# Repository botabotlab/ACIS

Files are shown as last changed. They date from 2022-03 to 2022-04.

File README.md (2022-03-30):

# AMIS
AMIS : an open-source Autonomous MultiWell Imaging Station



# Build instructions

## Server

The following software must be installed for the server to work properly. The installation has been tested on different machines with ARM or X86 architecture based on Ubuntu or Debian distributions:

-   **[Mosquitto](https://github.com/eclipse/mosquitto)** : allows devices to communicate with each other using the MQTT protocol)
-   **[NodeJS 16](https://github.com/nodejs/Release)** (recommended version) : required runtime for the automation software
-   **[Node-RED](https://github.com/node-red/node-red)** : (automation server and graphical interface
-   **[Motion](https://github.com/Motion-Project/motion)** (not mandatory) : allows the creation of an IP camera to remotely retrieve the video stream from the microscope.
-   **[v4l2loopback](https://github.com/umlaeute/v4l2loopback)** : creation of virtual cameras that can be used for autofocus, image analysis, image display on screen or as an IP camera.
-   **[ffmpeg](https://github.com/FFmpeg/FFmpeg)** : duplicate the video stream of the USB camera in the virtual cameras
-   **[OpenCV-python](https://github.com/opencv/opencv-python)** : Image analysis library (python3 required)
    
Once Node-RED is installed and started, the user can access its graphical interface directly from the single board computer by entering http://127.0.0.1:1880 in the web browser or http://local.ip.of.the.SBC:1880 (if the interface is accessed from another computer). The "**[node-red-dashboard](https://github.com/node-red/node-red-dashboard)**" palette must be installed and the flow can be imported.

## Microcontroller

### Dependencies 

The microcontrollers code compilation and uploading can be done using the Arduino IDE. However, the Arduino IDE does not natively work with the ESP8266. The support for these boards must therefore be manually added by going to **File > Preference > Additional Boards Manager URLs** and pasting the following URL: "http://arduino.esp8266.com/stable/package_esp8266com_index.json" and installed by selecting ESP8266 in **Tools > Board > Boards Manager.**

3 libraries are required to run the code and can be found in the Arduino IDE library manager:

-   [PubSubClient](https://github.com/knolleary/pubsubclient)
-   [ArduinoJson](https://github.com/bblanchon/ArduinoJson)
-   [Adafruit_NeoPixel](https://github.com/adafruit/Adafruit_NeoPixel)
    
### SPIFFS 

To facilitate the setting of WiFi and restore the previous state of the LEDs even in case of the microcontroller restart, JSON files (wifi.json and state.json) are stored in the SPIFFS memory. The use of SPIFFS memory allows to modify these parameters without having to recompile and upload the code and the use of JSON files makes the editing of these files faster and more intuitive than modifying the source code. Access to SPIFF memory is also not integrated by default in the IDE. The ESP8266 file uploader plugin can be downloaded at the following address:

https://github.com/esp8266/arduino-esp8266fs-plugin and unzipped in a **"tools"** folder created in the working directory of the arduino IDE.

The folder structure should look like this : **< home_dir>/Arduino-<version> /tools/ESP8266FS/tool/esp8266fs.jar)**. The arduino IDE can then be restarted and the tool should appear in **Tool > ESP8266 Sketch Data Upload.**

## Microscope

### Camera support

The camera support has been 3D printed in translucent ABS using a Prusa I3 MK3 (nozzle : 250°C, Bed : 100°C, nozzle 0.4mm, layer height : 0.2mm, filling 100%), however the parts can be printed in any type of plastic (PLA, PETG,...) using printers with lower tolerances and precision. The distance between the lens and the sensor is not critical, but the lens must be perpendicular to the sensor as well as the camera which must be perpendicular to the sample to avoid optical aberrations on the edge of the images. A manual adjustment of the parts using sandpaper may be necessary to compensate for small printing imperfections. The camera is held on the X axis of the printer with 3 neodymium magnets of 10x3mm.

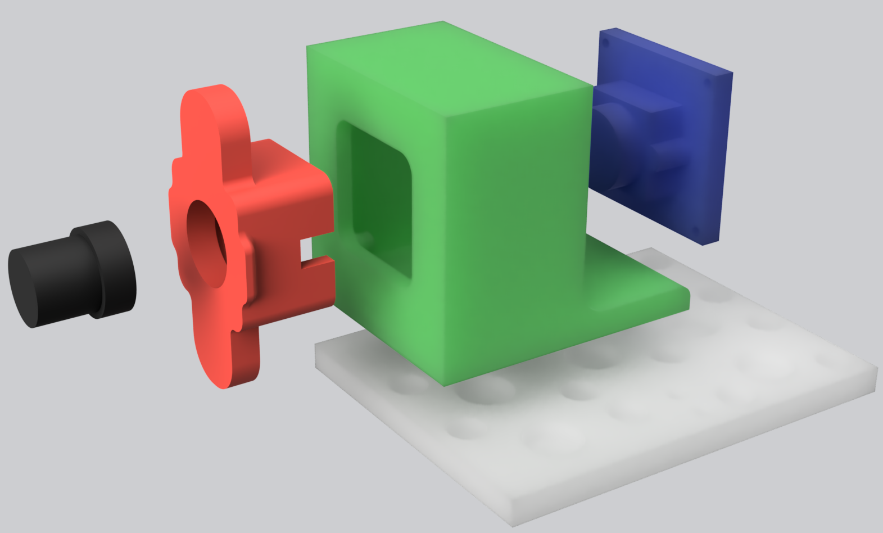
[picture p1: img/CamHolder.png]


Several digital camera models with different prices, sizes and resolutions were tested to realize the microscope. The following sensors (with prices ranging from 10€ to 50€) were tested : Omnivision OV2640, OV3660, OV4689 and OV5647 or Sony IMX179 and all gave similar results. We have also modified webcams that are easily found on the market such as Logitech c270 or c920 which work perfectly. However, we recommend the use of camera modules with an M12 mount compared to webcams ; the lens placement is easier and the generally square PCB (versus rectangular/oval for webcams) makes it easier to install the camera on the magnetic mount. The resolution has little importance on the captured image quality, although a higher resolution allows a greater digital zoom. The limiting system factor is not the sensor, but the optics. A resolution of 720p is thus largely sufficient and allows simplifying the image analysis, but a 1080p or 4k resolution can be used in case the user would like to perform a digital zoom in addition to the optical zoom. 

### Light

The lighting system is built by soldering 24 addressable LED SK6812 (Data OUT of one LED should be soldered on the Data In of the next one) the LED matrix thus created will be driven by an ESP8266 by soldering the VCC and GND of the LEDs on pin 5V and GND of the microcontroller and by connecting the Din of the first led on pin D5 (GPIO 14) of the ESP. The system will then be controllable in MQTT by the Node-RED server. 

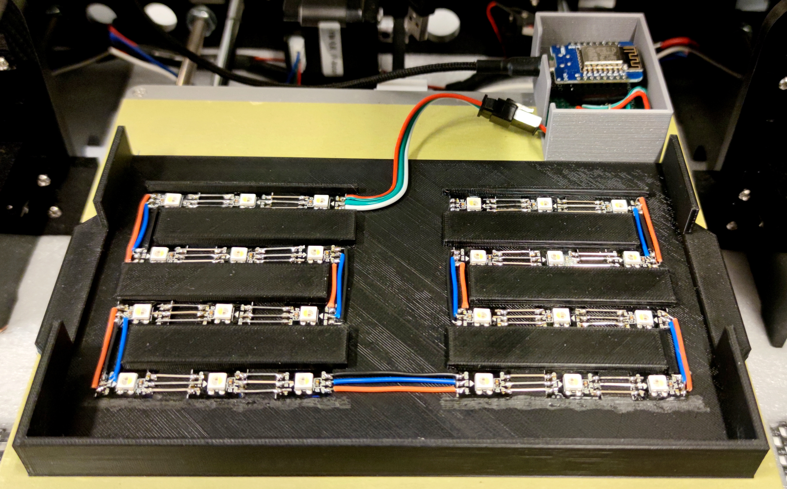
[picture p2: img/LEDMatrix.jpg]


The LED employed offer 4 light channels ; red, green, blue and cold white. We recommend using RGBW LED rather than RGB LED such as WS2812B. Although it is possible to obtain a relatively white light by combining the 3 RGB channels the positioning in 3 diodes makes that the light of each channel does not enter the medium with exactly the same angle of incidence and thus does form chromatic aberrations  These aberrations are not critical as the colored background will be removed by the thresholding adaptation step of the image analysis algorithm but it may affect the measurements if a quantification of the color of the algae is desired. The presence of a white channel mitigates this problem while offering a higher light intensity and preserving the accuracy of the colors (we recommend choosing SK6812 Neutral white and locking the white balance of the camera) . The color channels can be used to expose the sample to monochromatic or polychromatic light in order to improve the image contrast or to induce certain biological processes.

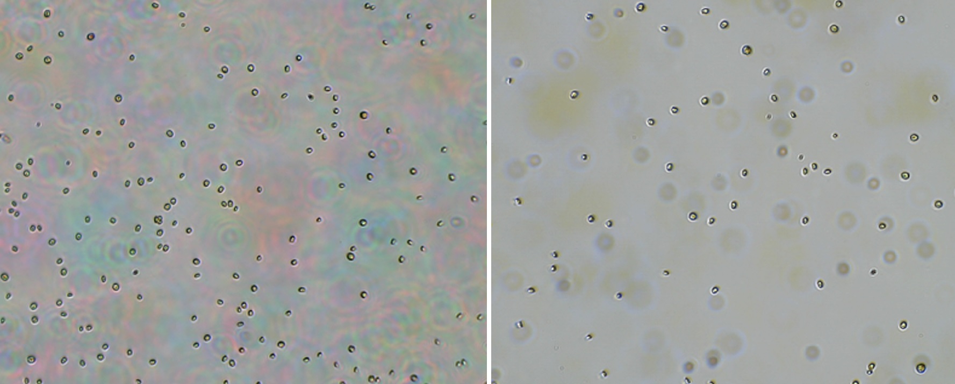
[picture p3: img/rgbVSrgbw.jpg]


*Chromatic aberration caused by the RGB light compared to a sample illuminated by a white light.*

## Pump

The system use a pump system described in a  [previous publication](https://www.sciencedirect.com/science/article/pii/S2468067221000286) . For the microscope, only one pump is needed and can be connected to a culture vessel (Erlenmeyer flask, photobioreactor) using a 7mm diameter autoclavable silicone tube. The tubing can be inserted into a micropipette tip for P1000 (blue tip). The pump can be primed until the liquid reaches the tip. The tip can then be placed on the magnetic tool holder and held in place with a 3D printed holder.

[Repository of the pump system](https://doi.org/10.17605/OSF.IO/ZP2S6) 

## 3D printer 

Our goal is to make a simple and universal system that can work with virtually any 3D printer model. A custom PCB would be complex, expensive and not very scalable. We therefore decided to exploit a common feature shared by many 3D printers. Indeed, these printers are generally controllable with standardized commands called GCODE. This set of instructions allows to control the machine movements on its 3 axes and to activate tools (plastic extruder, heating plate, fan, etc.).

Examples of GCode commands :
-   G91 : to set the machine in relative displacement
-   G0 X50 (move 50 mm along the x axis)

 [More info about GCode](https://reprap.org/wiki/G-code)

The commands can be sent via USB or placed in a text file on an SD card (or USB key) that will be read by the machine. 

A 3D printer only applies a simple sequence of commands and has no preconceived notions about their functions. It is therefore totally possible to remove the plastic extruder and replace it with a microscope and still be able to drive the machine using exactly the same commands. This is very interesting as it means that it is possible to transform a printer into a microscope, regardless of its brand, with almost no software or hardware modifications and to restore the original function of the machine if necessary.

### 3D printer hack

We chose an Anet A8 printer because its design is very simple, this model is easy to find on the internet and there are a lot of replacement parts and upgrades available. We kept most of the original parts (chassis, motors, print bed, motherboard). Instead of installing the extruder on the X axis we placed a 3D printed part with magnets to make a quick attachment for the camera or the sampling system. This part has been custom made for the Anet A8 and can not be used for another brand. However this modification is trivial and can be done on any 3D printer of the Cartesian or delta type. The only requirement is to have the camera perpendicular to the print bed (usually the Y axis).

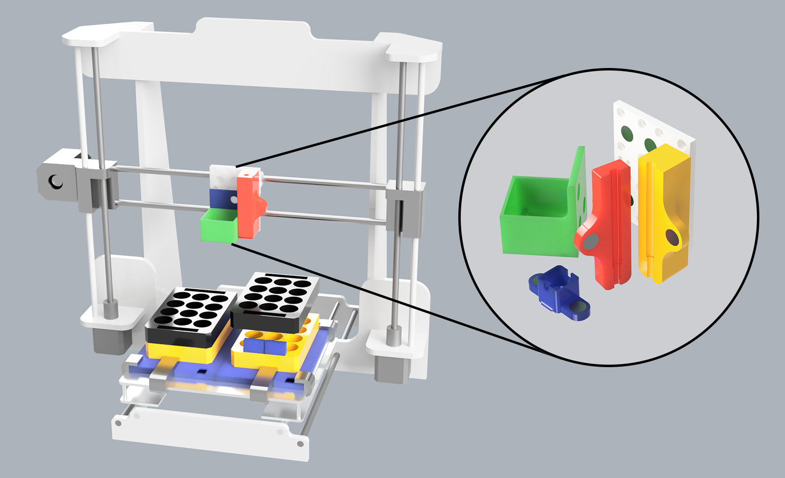
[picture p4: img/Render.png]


To automate and control the device remotely, we connected an ESP8266 on the serial port of the motherboard. This WiFI microcontroller, allows to send Gcode commands using the MQTT communication protocol. The communication is bidirectional, and it is therefore possible to control the machine but also to obtain information on its status such as the current position of the camera (an interesting feature to control the machine remotely). The microcontroller is removable connected to the motherboard using an FC10P  connector and can easily be removed to restore the printer original functions.



*Modification of the Anet A8 motherboard to be able to drive it in MQTT via its serial port. The motherboard has been set in "Serial" mode by bridging two pads (A) and then an ESP8266 (C ) has been connected to the VCC, GND, TX, RX of the motherboard (B). The serial connection between the microcontroller must be "crossed", meaning the TX of the ESP8266 connects to the RX of the motherboard and the RX connects to the TX.*

### Remote control using MQTT

MQTT (Message Queuing Telemetry Transport) is a publish/subscribe machine to machine communication protocol invented by IBM. Initially designed to retrieve information from remote locations from resource constrained devices (like as microcontroller) over an unreliable, high latency and low bandwidth connection (satellite connection for instance) (REF 29) this protocol is nowadays mainly used for IOT (Internet Of Things) applications. This widely used protocol offers numerous advantages for our application. It its simple to use, secure (message can be encrypted using TLS) , reliable, lightweight (in term of computing resources and bandwidth usage), compatible with virtually any programming languages (python, C, C#, C++, java, javascript, lua, ruby, rust, …) and highly scalable.

A typical MQTT communication requires at least 4 components:
-   **Publisher** :  the device that will send information or commands (a computer, a smartphone, a microcontroller)
-   **Subscriber** : the device that will receive the command (in our case a microcontroller connected to the robot)
-   **Broker** : the server that links the different devices
-   **Internet router**
    
*A publisher can also subscribe to one or more topics and that a bidirectional communication between the devices is possible*.

In most universities and corporate networks, some ports may be blocked (even locally) which will prevent MQTT (running on port 1883) from working. We recommend using a router over which the user has full control to create a local subnet to which devices can connect without restriction. The use of an ESP32/8266, a smartphone or a computer in access point mode can also be a solution to create a local network. An internet connection is not necessary as long as all devices are on the same network and port 1883 is not blocked. Our system is able to work locally without depending on a cloud, but an internet connection can be useful for remote control using a VPN (Virtual Private Network) or to host the broker in a VPS (Virtual Private Server).

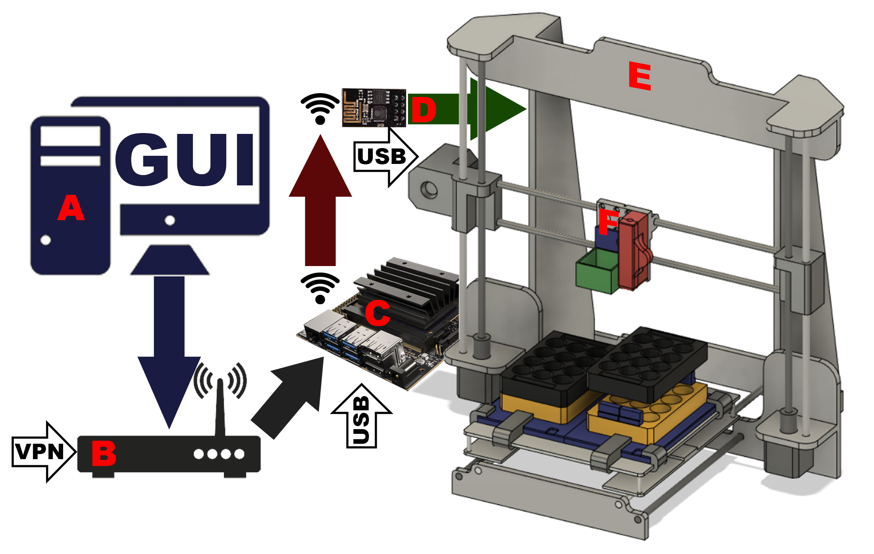
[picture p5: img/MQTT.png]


*Representation of the MQTT communication, allowing to control the microscope remotely. The graphical control interface accessible from a computer or a smartphone (A) connected to the laboratory router (B) allows formatting and send GCODE commands in WiFi to the MQTT broker installed on the Jeston Nano (C ) . The message is then connected to the ESP8266 (D) subscribed to the right topic and which will finally transmit the GCODE command in serial to the printer motherboard (E) allowing to move the camera (F).*

To send a command to the microscope, the user must publish the payload containing the command (e.g. G0 X50) with the topic corresponding to the microscope (microscope/room01/cmd/01) while being subscribed to the debug topic (microscope/room01/debug/01) to receive confirmation that the command is correct and has been applied. For our device, the microscope, the LED lighting system and the manipulation system are all 3 controllable by MQTT.

If the user does not want to use a MQTT connection, our microscope can be completely controlled using a serial communication. Simply connect the signle board computer to the 3D printer using an usb cable and replace the MQTT node with a Serial out node (by installing the "node-red-node-serialport" node) and select the com port (e.g. /dev/ttyUSB0) and baud rate (115200). Since the commands sent have the same structure as GCODE commands, no software modification is necessary. The same applies to the LED array, which can be connected to the Jetson nano via USB and driven via serial.

# Control

The control of the machine can be done in three different ways:

-   Manual remote control by sending messages in MQTT using the software/programming language chosen by the user
-   Manual control from the Node-RED graphical interface
-   Automatic control using a JSON config file

## MQTT Custom control

The two following examples of topics "**microscope/01/move**" and "**microscope/01/light**" manage respectively the microscope and the lighting system thanks to the MQTT Custom control.

The commands sent to the topic "microscope/01/move" must have exactly the same structure as GCODE commands. 

|CMD|Description  |
|--|--|
| M17 | Enable stepper motors |
|M18 | Disable stepper motors|
|M112 | Emergency stop|
|M114 | Get current position|
|G28 | Home|
|G90 | Absolute positioning|
|G91 | Relative positioning|
|G1Axis[X/Y/Z] Position(mm) Feed(optional) | Movement (Ex : G1 X10 Y20 Z30)|
    
*Frequently used GCODE commands*

## Graphical user interface

Once the Node-RED server is launched and the provided flow is deployed, the user can go to the address **http://server.ip:1880/ui** using a smartphone or computer and to access the Node-RED GUI.

*Graphical control interface via Node-RED composed of 5 panels (debug cam, light, control, plate and cam). The first panel (A) allows access to the security camera (Cam) to remotely view the machine to ensure it is working properly or to access the microscope image (Microscope) to observe the samples. The second panel allows to control the light either by choosing a color with the color picker (B) or by manually entering the RGB values (C). The control panel (D) allows you to manually move the camera on its 3 axes and returns the current position of the camera. The flat menu (E) allows you to move the camera to pre-programmed positions or to choose which well to light. The "SP" (safe position) button sends the camera to the upper right corner of the robot and advances the plate towards the user, thus facilitating the installation of multi-well plates, while the "LP" (last position) button returns the camera to its previous position (in case the user accidentally moves the camera). The panel (F) allows you to name the images. If several images are captured, the name will automatically be changed by adding the number of the photo (Iter). Finally, panel (G) allows you to perform autofocus and also to program the taking of multiple images separated by a defined delay.*

The camera can be started on the "**Developper camera**" menu. 

*The "Create virtual Cam" button allows to use “v4l2loopback” to create virtual cameras that will be used by different capture, image analysis, autofocus or debugging programs in HDMI or via IP stream. The use of virtual cameras is necessary because several programs cannot access the same camera at the same time. The second button allows to launch motion which will create an IP stream allowing to access the images remotely in the graphical interface. The button "copy usb webcam" will launch “ffmpeg” which will clone the physical camera in the different virtual cameras. The buttons CAM LCD ON and OFF allow the microscope image display or hiding through HDMI. Analyze ON and OFF display the image analysis (counting and size measurement) in real time on the HDMI output . Finally, the WB lock button and the WB slider allow to lock the white balance to a fixed value defined by the user. When the system is functional the 3 menus should be green.*

This graphical interface allows a quick and manual observation, capture and analysis of one or more samples. A typical use would be to place different samples in multi-well plates, turn on the microscope, initialize the cameras, send the camera to "**Safepos**", place the plates on the bed, choose the illumination color and observe the desired samples. This system is faster than a regular microscope using a slide/coverslip system. 

## Automation

Many situations may require the capture of a large number of images (capture of several plates in a row) or need to be done over a long period of time (real time monitoring of a culture). As manually preparing and analyzing the samples is not feasible in this case, we have developed an automation system. This system allows to automate all the actions available on the graphical interface based on a JSON structure that is both intuitive and flexible. The user can thus define the sequence name, the wells to fill (if filling is desired) and the need to purge the circuit or not (to avoid contamination if the time between two samples is high), the wells to capture (if capturing is desired) and the light (color and intensity) corresponding to each well and the time between two samplings or captures.

JSON structure :

	{  
	"name" : "Name of the experiment",  
	"pos" : [ [X1 (0-5) ,Y1(0-3)] ],  
	"light": [ [R(0-255) , G(0-255) , B(0-255), W(0-255)] ],  
	"delay":[(s)],  
	"capture":true-false,  
	"sampling":true-false,  
	"volume":[(ml)]  
	"trash":true-false  
	}

The order of the wells can be defined by the user and not all wells have to be used ; it is possible to fill a complete plate or just a column. The light can be different between each well. To do this it is imperative that the "light" array has exactly the same length as the "pos" array. If the same color intensity should be used for all wells it is possible to enter only one light value in "light" and the system will automatically apply the light to all wells.

It is not mandatory to capture images ; the machine can for example be used to fill multi-well plates with samples. To do so, you just have to set the "capture" key to false. The following JSON allows to fill 1 multiwell plate with a volume of 2ml (this procedure takes about 2 minutes for 12 wells). Capturing images alone without taking a sample is also possible ; the "capture" property must be set to true.

Demo script to fill the plate 1 with samples of 1ml : 

	{
	"name" : "Fill plate 1",
	"pos":[
	[0,0],[1,0],[2,0],
	[0,1],[1,1],[2,1],
	[0,2],[1,2],[2,2],
	[0,3],[1,3],[2,3]
	],
	"sampling":true,
	"volume" : [1]
	} 

Demo script to capture the plate 1 with a white light of 100% :

	{
	"name" : "Capture plate 1",
	"pos":[
	[0,0],[1,0],[2,0],
	[0,1],[1,1],[2,1],
	[0,2],[1,2],[2,2],
	[0,3],[1,3],[2,3]
	],
	"capture":true,
	"light":[[0,0,0,255]]
	}

### Example

The following example describes the most complex measurement sequence currently achievable with the machine consisting in reading three samples with different parameters. The robot will automatically fill the wells with three different volumes (1ml 2ml and 3ml) while purging the silicone tube between two samples. Each sample will be observed with a different color (red, green and blue) and intensity (100%, 50% and 25%) and the time between two measurements is set to 30 seconds for the first sample sample and 1 minute for the second one : 

	{
	"name" : "DemoSeq", 
	"pos" : [[0,0],[2,3],[3,0]], 
	"light" : [[255,0,0,0],[0,255,0,0],[0,0,255,0]], 
	"delay" : [30,60,0] , 
	"sampling" : true, 
	"volume" : [1,2,3], 
	"trash" : true, 
	"capture" : true
	}

## Safety

- The system uses a 220V power supply so the connections must be properly isolated. 
- The motherboard as well as the single board computer and the lighting system must be kept away from humidity or any conductive elements that could cause a short circuit. 
- The 3 axes of movement must not be obstructed as most 3D printers do not have built-in stall detection (meaning that the motors can be forced even if they are blocked) and the limit switches must be accessible during calibration. 
- The user must always check that the magnets are well aligned when a tool is placed on the machine, taking care not to get his fingers caught when installing the tools as the magnets are relatively powerful.

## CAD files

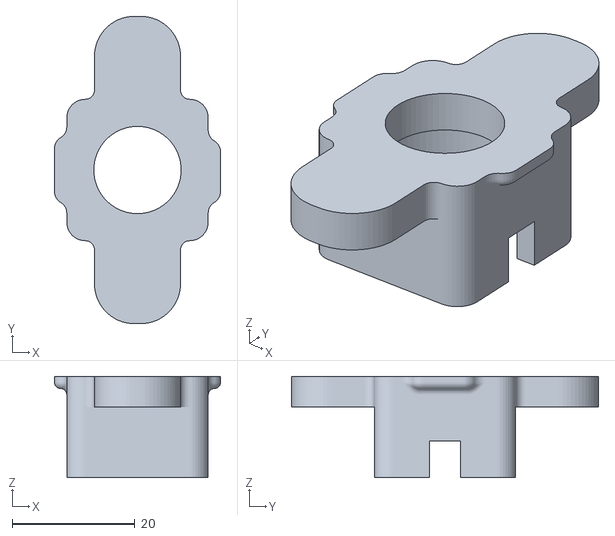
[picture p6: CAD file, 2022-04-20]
3Dfiles/Lens_holder_V2.stl
27.0 x 50.0 x 16.5

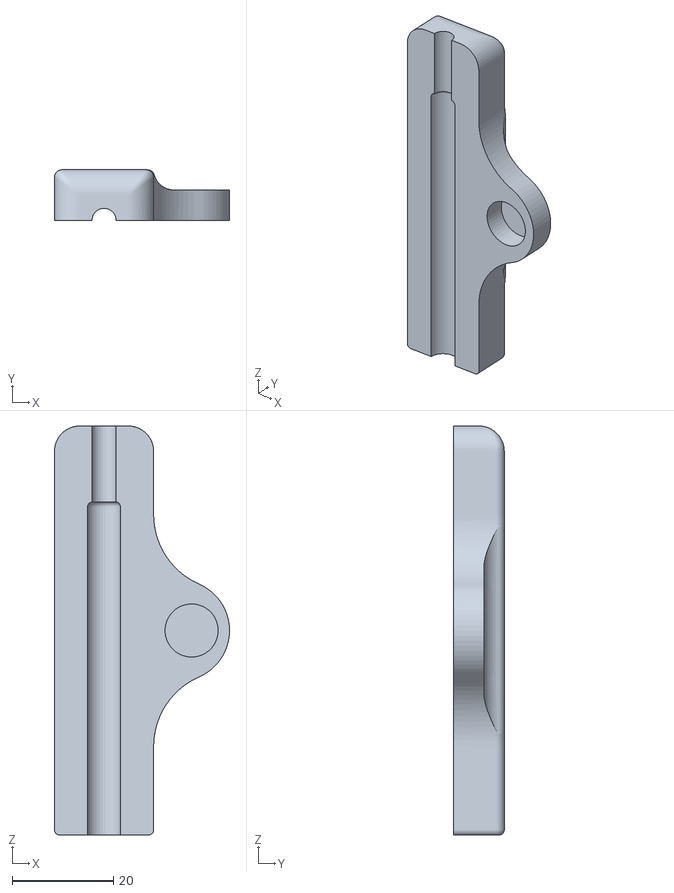
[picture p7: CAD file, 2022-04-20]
3Dfiles/Pipette_V1B.stl
34.6 x 10.0 x 80.8

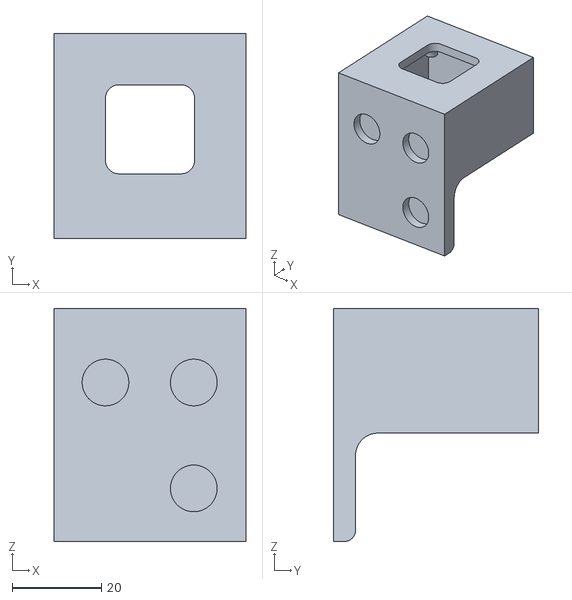
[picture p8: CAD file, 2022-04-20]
3Dfiles/Cam_body_V1.stl
43.0 x 46.2 x 52.4

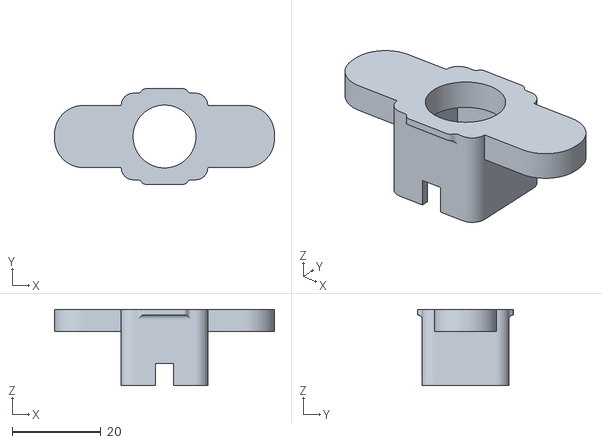
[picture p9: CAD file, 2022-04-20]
3Dfiles/Lens_holder_V1.stl
49.5 x 21.5 x 17.2

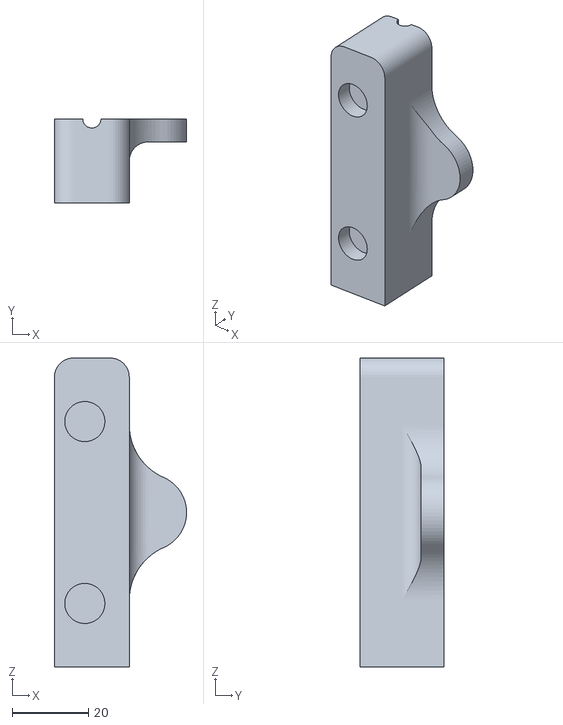
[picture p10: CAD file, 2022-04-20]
3Dfiles/Pipette_V1A.stl
34.6 x 22.0 x 80.8

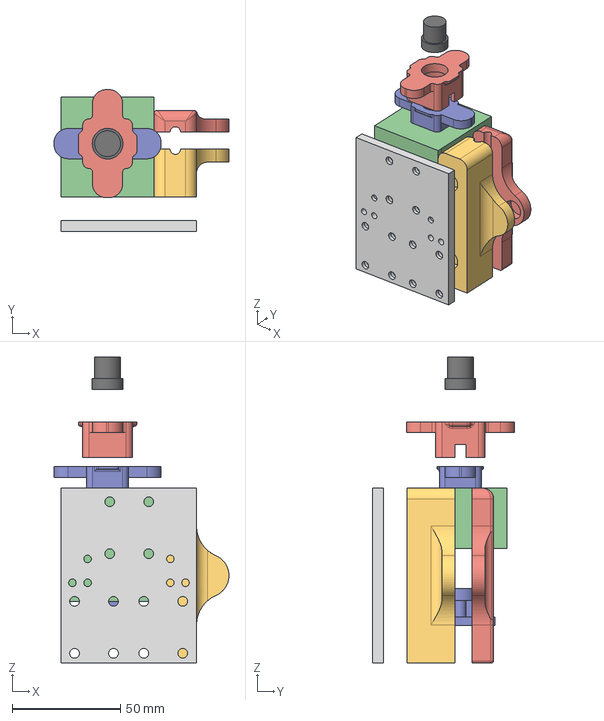
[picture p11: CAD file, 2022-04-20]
3Dfiles/Camera_Pipette_magnetic-holder.step
80.9 x 65.6 x 141.4 mm

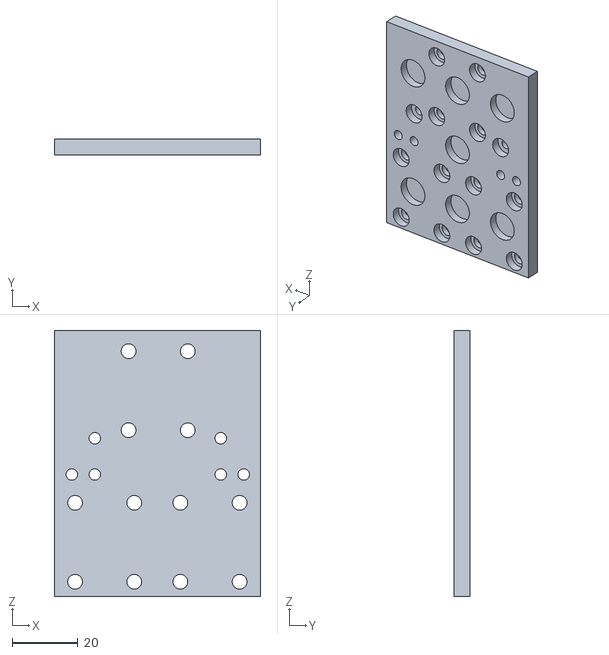
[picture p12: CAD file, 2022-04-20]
3Dfiles/AnetA8_magnetic_holder.stl
62.7 x 5.00 x 80.8

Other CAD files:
3Dfiles/Cam_body_V2.stl

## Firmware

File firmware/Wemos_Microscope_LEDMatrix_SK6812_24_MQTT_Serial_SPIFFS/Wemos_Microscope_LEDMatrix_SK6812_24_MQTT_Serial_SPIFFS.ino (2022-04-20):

//Dependencies
//--------------------------------------
#include <Arduino.h>
#include <ESP8266WiFi.h>
#include <WiFiClient.h>
#include <ESP8266WebServer.h>
#include <PubSubClient.h>
#include <DNSServer.h>
#include "FS.h"
#include <ArduinoJson.h> //ArduinoJSON6
#include <Adafruit_NeoPixel.h>
//--------------------------------------

//WiFi Settings
//----------------------------------------------------------------------------------------
const IPAddress apIP(192, 168, 1, 1);
const char* apSSID = "Microscope_SK6812";
boolean SettingMode = false;
String ssidList;
int maxtry = 30;
DNSServer dnsServer;
ESP8266WebServer webServer(80);
const char *ssid, *password, *mqtt_server, *mqtt_user, *mqtt_pass, *topic_led, *topic_all, *HostName;
DynamicJsonDocument WIFI(2048);

WiFiClient espClient;
PubSubClient client(espClient);
bool WiFiConnected = false;
//----------------------------------------------------------------------------------------

//#define FASTLED_INTERNAL

#define NUM_LEDS 24
#define LED_PIN 14
Adafruit_NeoPixel LED(NUM_LEDS, LED_PIN, NEO_GRBW + NEO_KHZ800);
//CRGB LED[NUM_LEDS];

DynamicJsonDocument CMD(2048);
DynamicJsonDocument STATE(2048);

int MatrixPos[][6] = {
  {2,1,0,23,22,21},
  {3,4,5,18,19,20},
  {8,7,6,17,16,15},
  {9,10,11,12,13,14},
};

//MQTT
//-------------------------------------------------------------------
void MQTT_loop() {
  if (WiFiConnected == true) {
    if (!client.connected()) {
      reconnect();
    }
    client.loop();
  }
}

void callback(String topic, byte* message, unsigned int length) {
  String messageTemp;
  for (int i = 0; i < length; i++) {
    messageTemp += (char)message[i];
  }
  Serial.print("Topic : ");
  Serial.println(topic);
  Serial.print("Payload : ");
  Serial.println(messageTemp);
  Settings(topic, messageTemp);
}
//-------------------------------------------------------------------

//LED Settings
//-------------------------------------------------
void Settings(String topic, String messageTemp) {
  deserializeJson(CMD, messageTemp);
  int X = 0, Y = 0, R = 0, G = 0, B = 0, W = 0;
  if (CMD.containsKey("R")) {
    R = CMD["R"];
  }
  if (CMD.containsKey("G")) {
    G = CMD["G"];
  }
  if (CMD.containsKey("B")) {
    B = CMD["B"];
  }
  if (CMD.containsKey("W")) {
    W = CMD["W"];
  }
  if (CMD.containsKey("X")) {
    X = CMD["X"];
  }
  if (CMD.containsKey("Y")) {
    Y = CMD["Y"];
  }
  if (topic == topic_led) {
    //LED[MatrixPos[Y][X]] = CRGB( R, G, B);
    LED.setPixelColor(MatrixPos[Y][X], LED.Color(R, G, B , W));
    STATE[MatrixPos[Y][X]]["R"] = R;
    STATE[MatrixPos[Y][X]]["G"] = G;
    STATE[MatrixPos[Y][X]]["B"] = B;
    STATE[MatrixPos[Y][X]]["W"] = W;
    save_state();
  }
  if (topic == topic_all) {
    //fill_solid(LED, NUM_LEDS, CRGB( R, G, B));
    LED.fill(LED.Color(R, G, B , W), 0, NUM_LEDS);
    for (int i = 0; i < 25; i++) {
      STATE[i]["R"] = R;
      STATE[i]["G"] = G;
      STATE[i]["B"] = B;
      STATE[i]["W"] = W;
    }
    save_state();
  }
  //FastLED.show();
  LED.show();
}

//-------------------------------------------------
void setup() {
  //FastLED.addLeds<WS2811, DATA_PIN, GRB>(LED, NUM_LEDS);
  LED.begin();
  Serial.begin(115200);
  Serial.println();
  Serial.setTimeout(500);

  if (!SPIFFS.begin()) {
    Serial.println("An Error has occurred while mounting SPIFFS");
    return;
  }

  load_wifi();
  WiFiConnected = setup_wifi();
  client.setServer(mqtt_server, 1883);
  client.setCallback(callback);
  load_state();
  restore_state();
}

void loop() {
  MQTT_loop();
  if (Serial.available()) {
    String input = Serial.readString();
    String Select = input.substring(0, 1);
    String Command = input.substring(1);

    //HELP
    //....................................
    if (Select == "H" || Select == "h") {
      Serial.println("-------------------------------------------------------------");
      Serial.println("Available commands :");
      Serial.println("H or h : Help");
      Serial.println();
      Serial.println("R or r : Start a Web UI to edit de WiFi/MQTT settings");
      Serial.println();
      Serial.println("W or w + JSON: Edit the WiFi/MQTT With the provided JSON");
      Serial.println("Example : W {\"SSID\": \"WiFi SSID\", \"Pass\":\"WiFi Pass\", \"MQTT_Server\":\"Broker.IP\", \"MQTT_Pass\":\"Broker.Pass\", \"Topic_LED1\":\"topic/led/01\", \"Topic_LED2\":\"topic/led/02\", \"HostName\":\"HostName\"}");
      Serial.println();
      Serial.println("A or a + JSON : Control the whole box");
      Serial.println("A {\"R\":0-255, \"G\":0-255, \"B\":0-255, \"W\":0-255 }");
      Serial.println("Example : A {\"R\":255, \"G\":0, \"B\":0, \"W\":0 }");
      Serial.println();
      Serial.println("XYRGB JSON : Control one LED");
      Serial.println("{\"X\": 0-4, \"Y\": 0-4, \"R\":0-255, \"G\":0-255, \"B\":0-255, \"W\":0-255 }");
      Serial.println("Example : {\"X\": 2, \"Y\": 2, \"R\":255, \"G\":0, \"B\":0, \"W\":0 }");

      Serial.println();
      Serial.println("0 : Turn OFF Matrix");
      Serial.println("-------------------------------------------------------------");
    }
    //....................................

    //RESET WiFI Settings and start web GUI
    //....................................
    if (Select == "R" || Select == "r") {
      SettingMode = true;
      SetupMode();
    }
    //....................................

    //Edit WiFi Settings from Serial
    //.............................................
    if (Select == "W" || Select == "w") {
      deserializeJson(CMD, Command);
      if (CMD.containsKey("SSID")) {
        WIFI["SSID"] = CMD["SSID"];
      }
      if (CMD.containsKey("Pass")) {
        WIFI["Pass"] = CMD["Pass"];
      }
      if (CMD.containsKey("MQTT_Server")) {
        WIFI["MQTT_Server"] = CMD["MQTT_Server"];
      }
      if (CMD.containsKey("MQTT_Pass")) {
        WIFI["MQTT_Pass"] = CMD["MQTT_Pass"];
      }
      if (CMD.containsKey("Topic")) {
        WIFI["Topic"] = CMD["Topic"];
      }
      if (CMD.containsKey("HostName")) {
        WIFI["HostName"] = CMD["HostName"];
      }
      save_wifi();
    }
    //.............................................

    //Serial Control one LED
    //................................
    if (Select == "{") {
      Settings(topic_led, input);
      Serial.print("CMD : ");
      Serial.println(input);
    }
    //................................

    //Serial Control ALL
    //................................
    if (Select == "A" || Select == "a") {
      Settings(topic_all, Command);
      Serial.print("CMD : ");
      Serial.println(Command);
    }
    //................................

    //Serial Control ALL
    //................................
    if (Select == "0") {
      Settings(topic_all, "{\"R\":0,\"G\":0,\"B\":0,\"W\":0}");
      Serial.print("CMD : ");
      Serial.println(Command);
    }
    //................................

    //Serial Control ALL
    //................................
    if (Select == "S" || Select == "s") {
      restore_state();
    }
    //................................

    Serial.read();
  }
}
